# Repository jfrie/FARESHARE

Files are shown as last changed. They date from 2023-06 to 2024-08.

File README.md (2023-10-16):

# FARESHARE
Fluid tracking in socially housed rats



## Contents of Repository
- Build instructions
- 3D print files
- Arduino code
- PCB GERBER file

## Description
Social factors have been shown to play a significant role in alcohol consumption. Studying the role of social context on alcohol drinking is important to understand the factors that contribute to initiation or maintenance of casual and problematic alcohol use. A large body of preclinical research has shown that social environment plays an important role in alcohol consumption and preference, though the extent of these effects have been obfuscated by methodological differences and technical challenges. Robust individual differences in alcohol intake in socially housed animals are difficult to track when animals share a common fluid source. Commercial solutions are prohibitively expensive and are limited by proprietary software and hardware. Here we describe an affordable, open-source solution for tracking fluid consumption in socially housed rats. The device uses RFID to identify rats, a lickometer to activate fluid delivery, a custom low-profile PCB that sits on top of an Arduino-based microcontroller, fluid delivery via custom peristaltic pump for accurate measurement of consumption volume, OLED display, and continuous data logging to an SD card. Having a robust, affordable method for measuring drinking in socially housed animals will be of considerable use in preclinical addiction research and a step toward more translationally relevant animal models of fluid consumption. The added dimension of time allows for the analysis of circadian-linked consumption and the discrimination of continuous or binge-like drinking behaviours. Additionally, being open-source enables researchers to customize the device for more advanced applications such as sending signals to additional peripherals (e.g., optogenetic stimulation) or software on drinking initiation for time-locked or closed-loop interventions, manipulations, and measurements.

Citing FARESHARE: A preprint introducing the software is available on bioXriv, which should be cited accordingly. https://www.biorxiv.org/content/10.1101/2023.10.06.561248v1.full

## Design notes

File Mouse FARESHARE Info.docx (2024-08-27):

Mouse FARESHARE

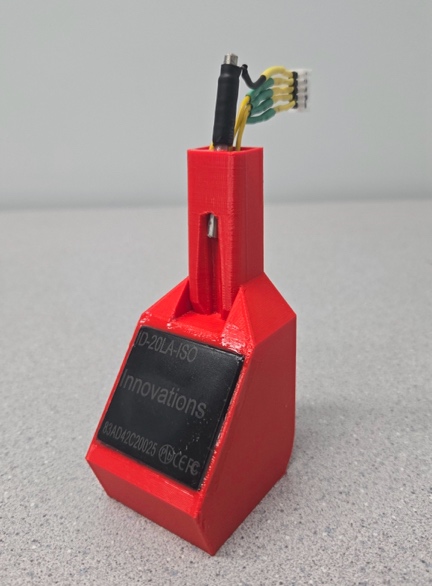
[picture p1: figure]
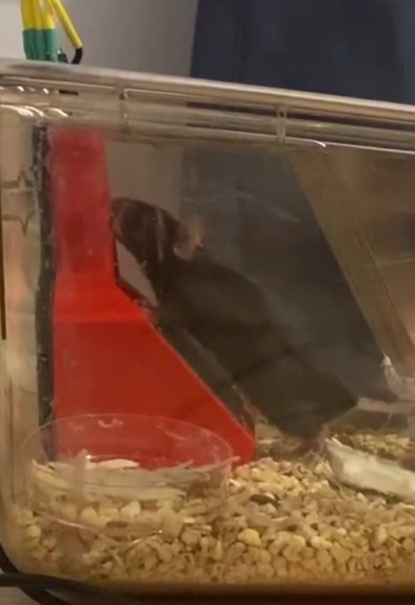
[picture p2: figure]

The mouse version of FARESHARE includes two notable design changes:

1) The scanner is now located below the subject such that the RFID tag can be placed on the chest. This frees the head for in vivo neural manipulation and recording.
2) Each lick now activates the motor such that increasing lick frequency increases fluid delivery. This means the licking microstructure is more meaningful, as the licking is driving fluid delivery, rather than just subject presence (with constant flow) as was the case previously.

The only major changes in instrumentation are the RFID housing print file, the scanner, and the straw.

The housing is now a single print. If printed upright (i.e. the direction it will be when used), it does not require any supports. We tried other designs, but mice would either find ways to cover the scanner, not align the tag properly, or just not use it.

The scanner used is now the larger ID20LA:

https://www.sparkfun.com/products/11828

Alternatively, ID20LA-ISO can be ordered directly from ID Innovations:

https://www.id-innovations.com/Modules(non%20write).htm

This is the same scanner but is compatible with the more standard ISO RFID tags that are commonly used in pets.

The straw is much smaller than the one used previously in rat version. We used these: https://www.amazon.ca/Unifizz-Stainless-Capillary-Seamless-Decoration/dp/B09PCY1L8N/ref=sr_1_13?keywords=stainless%2Bsteel%2Btube%2B3.2mm%2Bid&sr=8-13&th=1)

However, any 3.2mm ID, 4mm OD straw that is conductive will work. We cut them down to 5cm long with a Dremel. This size has the advantage of making a good seal with the tubing such that fluid does not drip through the straw, and rather is released in a more controlled droplet at the tip of the straw.

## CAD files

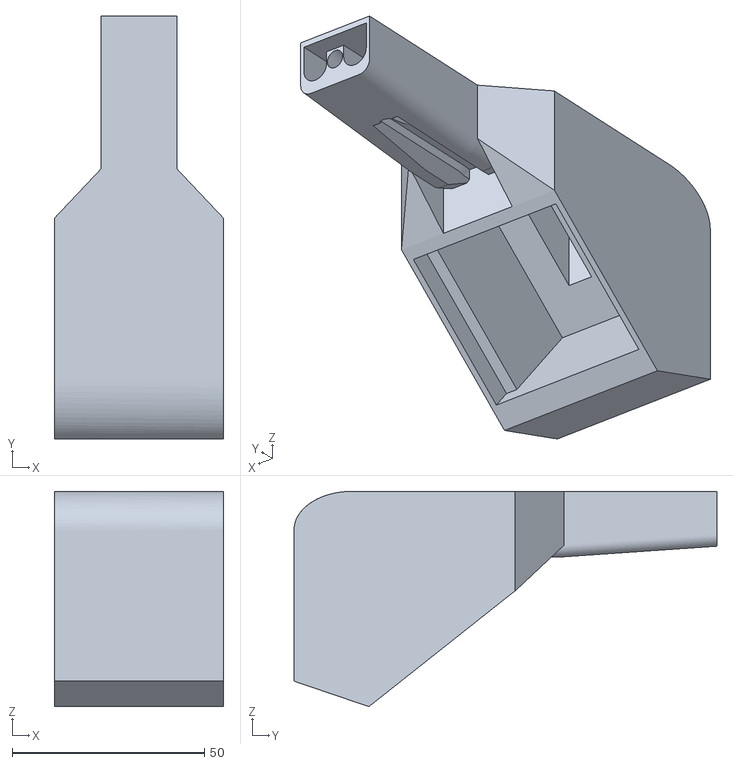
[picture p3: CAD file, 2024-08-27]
3D print files/Mouse RFID Housing.STL
44.0 x 110.0 x 56.0

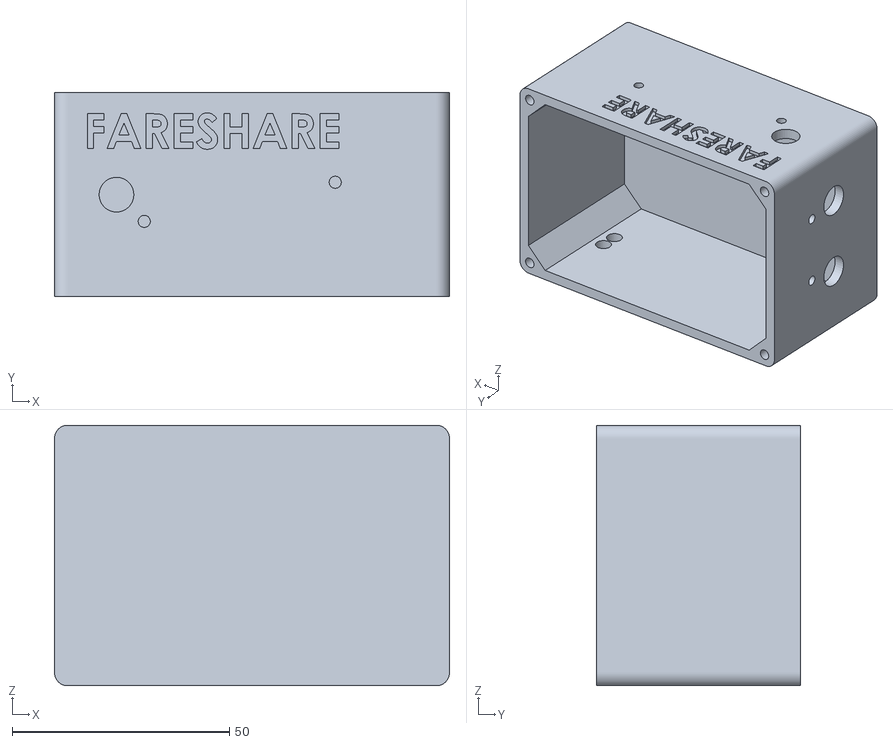
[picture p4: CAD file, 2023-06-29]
3D print files/Box.STL
91.0 x 47.0 x 60.0

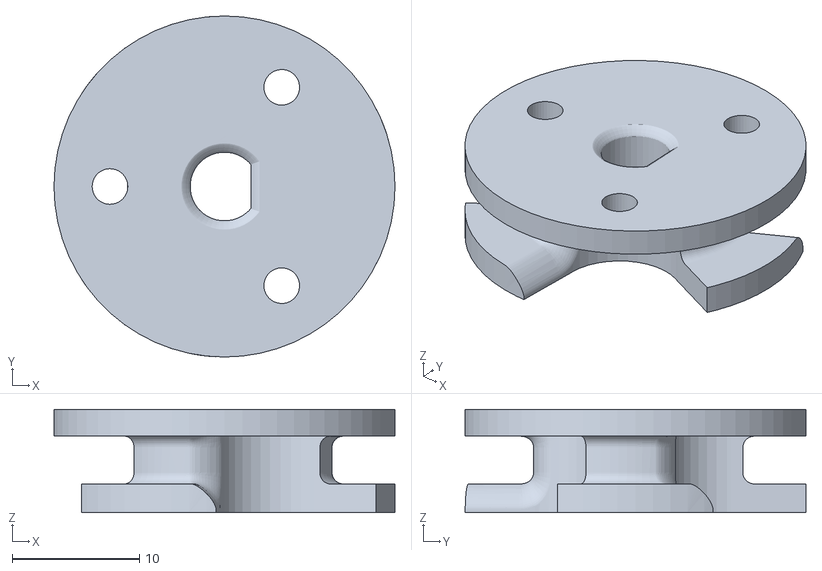
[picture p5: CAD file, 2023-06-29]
3D print files/Rotor.STL
26.8 x 26.8 x 8.10

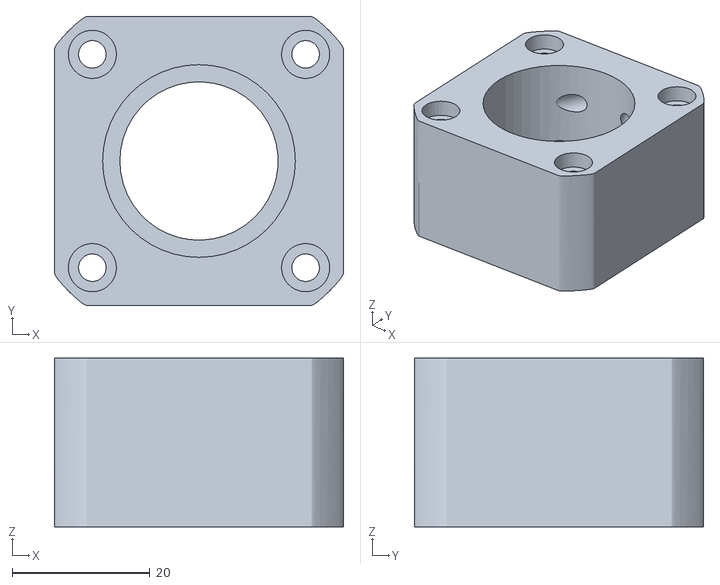
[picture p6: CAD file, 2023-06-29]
3D print files/Pump Case.STL
42.0 x 42.0 x 24.5

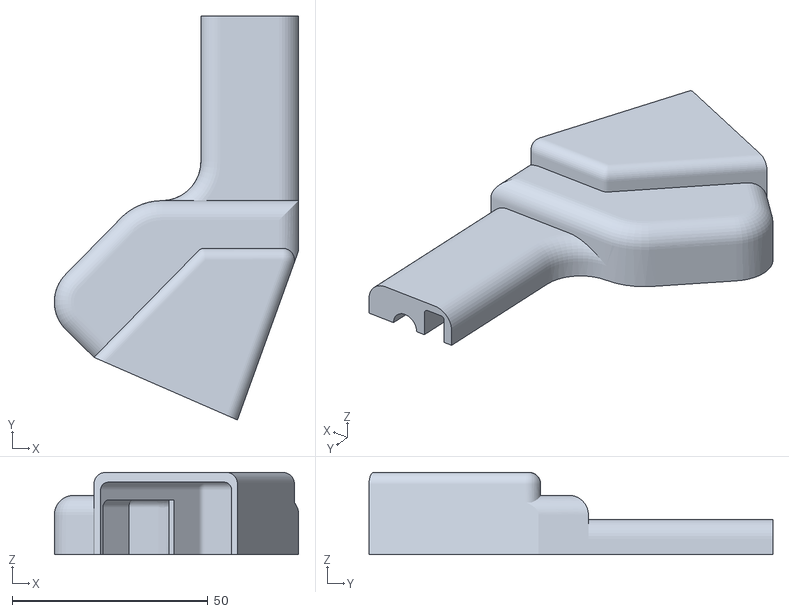
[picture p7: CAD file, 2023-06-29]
3D print files/RFID Housing Right.STL
62.4 x 103.2 x 21.0

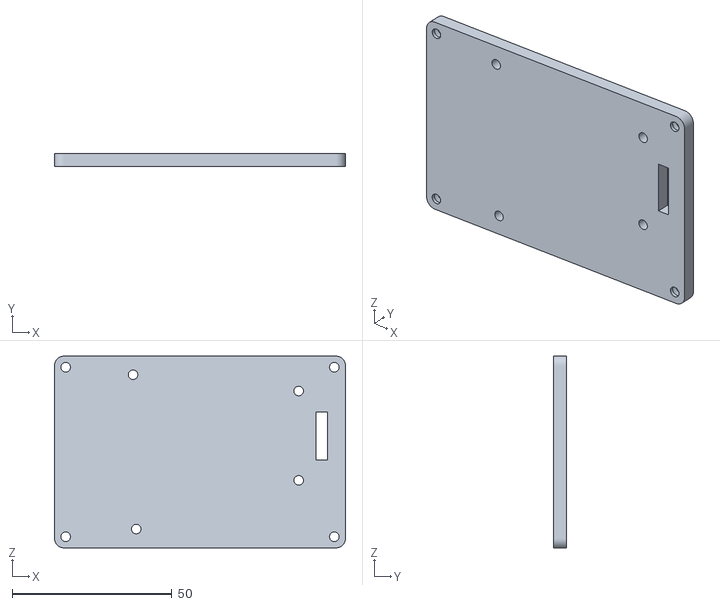
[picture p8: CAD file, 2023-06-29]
3D print files/Box_lid.STL
91.0 x 4.00 x 60.0

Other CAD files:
3D print files/RFID Housing Left.STL

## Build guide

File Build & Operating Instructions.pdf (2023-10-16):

Build Instructions

Table 1: Bill of Materials

Part Name | Distributer | Alternate | Cost ($US)
1000uF Capacitor (through hole) | Mouser | Digikey | 1.63
16G Needles (x2) | Fisher Scientific | Surgo | 0.85
1M Ohm Resistor (through hole) | Mouser | Digikey | 0.42
5-pin 2.54mm JST Female to Female
Cable | Walmart | Amazon | 1.30
5-pin 2.54mm JST Male header (x2) | Walmart | Amazon | 0.14
3D printer filament | Amazon | Hatchbox | 2.50
A4988 Stepper Motor Driver | Amazon | Digikey | 1.20
Ball bearings (3mm x 8mm x 4mm) (x4) | Amazon | NewEgg | 2.00
Barrel Jack PCB mount (3 pin) | Mouser | Digikey | 1.25
Break Away Headers (2.54mm straight)
(41 pins) | Sparkfun | Mouser | 3.50
Custom PCB | JLCPCB | OSHpark | 2.00
Dual lock (10cm) | Amazon | Mouser | 1.50
Epoxy | Walmart | Amazon | 6.12
Hook-up Wire (22 AWG) | Sparkfun | Amazon | 2.95
M3 Screw (Hex Socket, 25mm) (x4) | Home Hardware Amazon | 2.75
M3 Screw (Hex Socket, 10mm) (x7) | Home Hardware Amazon | 3.25
M3 Screw (Hex Socket, 5mm) (x8) | Home Hardware Amazon | 3.50
M3 Nut (x3) | Home Hardware Amazon | 2.00
Masterflex® Microbore Pump Tubing, Platinum-Cured Silicone, 1.42mm ID, 3.12mm OD (16cm long) | Avantor | Fisher
| | Scientific | 2.30
Mini 4-pin Push Button | Mouser | Amazon | 1.00
Micro SD Card (FAT16 or 32, 64MB to
32GB) | Amazon | Walmart | 5.99
Nema 17 Stepper Motor (4 lead, 2A) (17HS19-2004S1) | Amazon | AliExpress | 13.99
Power Supply (12V, 3A) | Amazon | Walmart | 8.99
Qwiic Cable Kit | Sparkfun | Mouser | 8.95
Qwiic OLED Display (0.91 in, 128x32) | Sparkfun | Mouser | 10.95
Qwiic OpenLog | Sparkfun | Mouser | 18.50
RedBoard Qwiic | Sparkfun | Mouser | 21.50
RFID Chip Injector (2.12x12mm) | Amazon | AliExpress | 6.99
RFID Glass Capsule (125kHz) | Sparkfun | Mouser | 5.50
RFID Reader Breakout | Sparkfun | Mouser | 2.10
RFID Reader ID-12LA (125 kHz) | Sparkfun | Mouser | 32.50
Silicone Tubing 1.5mm ID x 3mm (140
cm) | Amazon | NewEgg | 6.99
Stainless Steel Straw (straight 5mm OD) | Amazon | Whisk | 0.60
Total | | | $185.71

PCB Ordering: Upload GERBER file to https://jlcpcb.com and order with default settings.

PCB Soldering: The figure below shows the PCB before (left) and after (right) soldering. The

PCB is silk screened and labeled such that soldering orientation and positioning is clear.

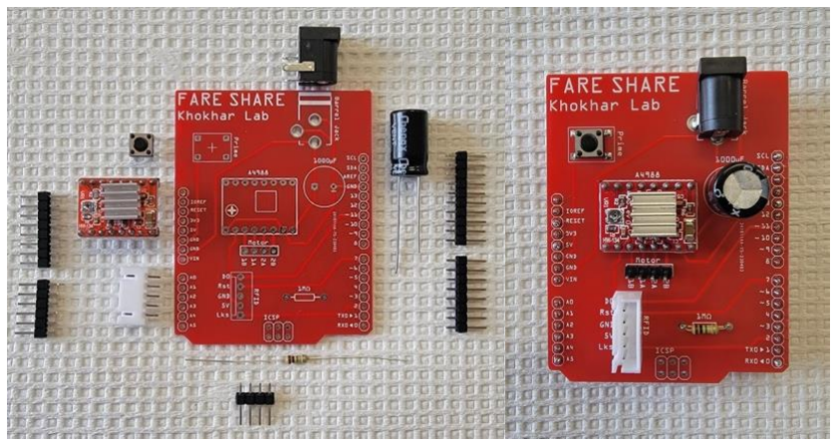
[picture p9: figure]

3D Printing: Print in the orientations shown below. The pump rotor and RFID housing should

be printed with supports. All other components can be printed without supports. Print with

standard PLA filament.

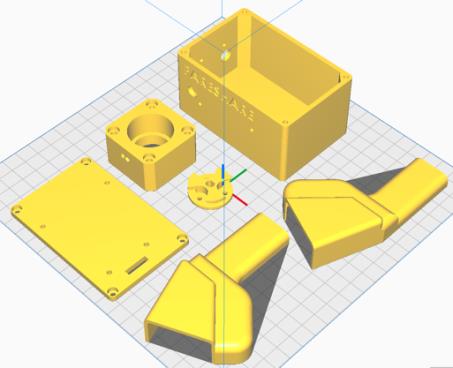
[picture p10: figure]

Pump Assembly:

1. Cut two 1cm pieces of needle by slowly rotating and cutting evenly so as not to

crimp.

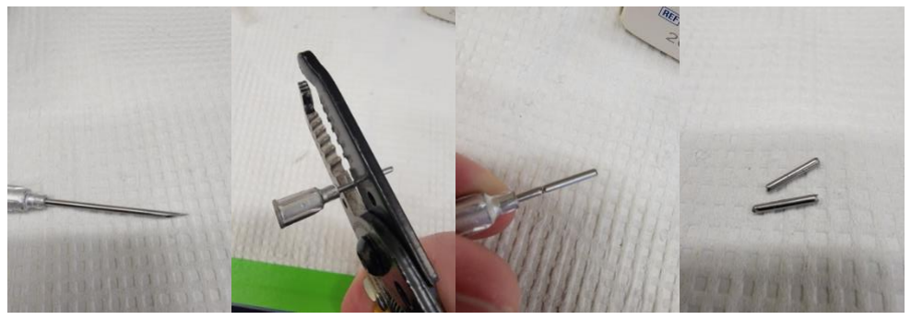
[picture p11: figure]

2. Screw M3X10 screws through the holes of the rotor

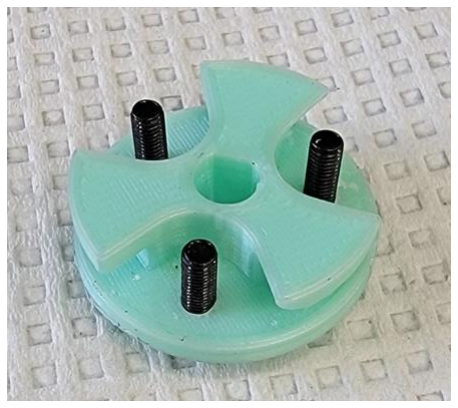
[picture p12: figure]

3. Place bearings on screws and secure with M3 nuts. Ensure the nuts are not too tight so

as to allow the bearings to turn without any friction.

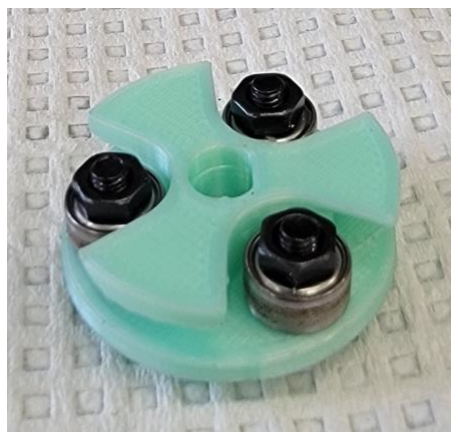
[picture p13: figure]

4. Thread 15cm segment of Masterflex tubing through pump case.

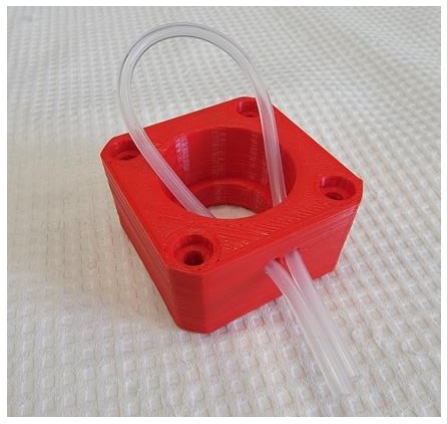
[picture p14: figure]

5. Wrap the tubing around the rotor and push the rotor into the pump housing while

keeping tension on the tubing. Once inside the housing, manually rotate the rotor a bit

and pull on each side of the tubing until the rotor is straight and the tubing wraps

around each bearing.

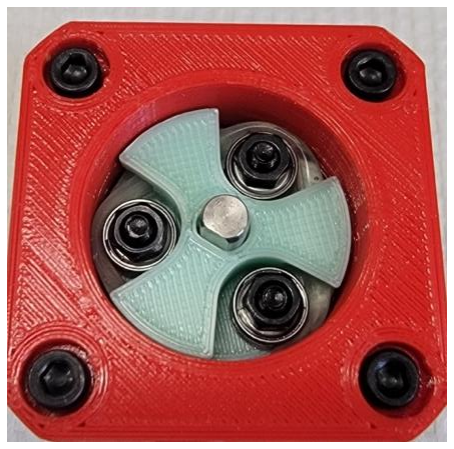
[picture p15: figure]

6. Thread another bearing onto the left (with tubing facing you) exiting tube.

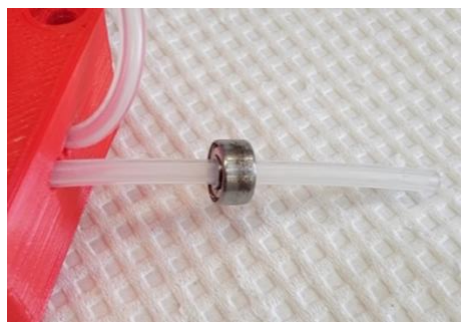
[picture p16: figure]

7. Bring bearing up to pump housing and epoxy or super glue to both tubing and

housing. This will keep the tubing from being pulled through the rotor or shifting.

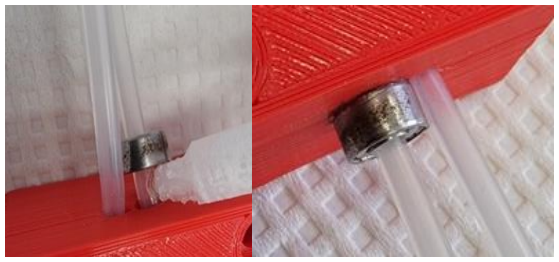
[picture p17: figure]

8. Insert needle segments halfway into tubing ends.

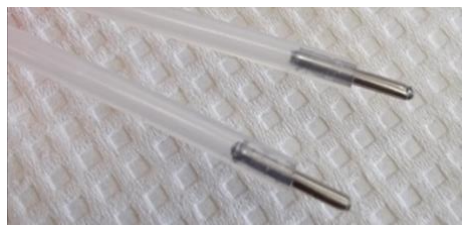
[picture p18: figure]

9. Place super glue where needle exits tubing and insert needle ends into two 70 cm

segments of silicon tubing (cheaper tubing), gluing tubes together.

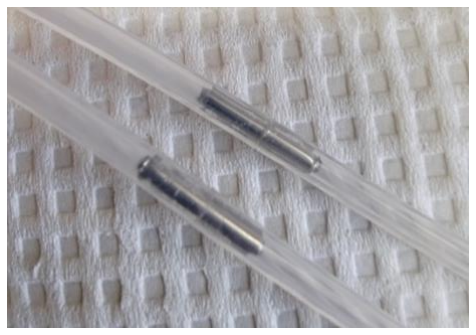
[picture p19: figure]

10. Place pump assembly onto motor with tubing facing the same direction as motor

wires and, using M3x25mm screws, fix in place.

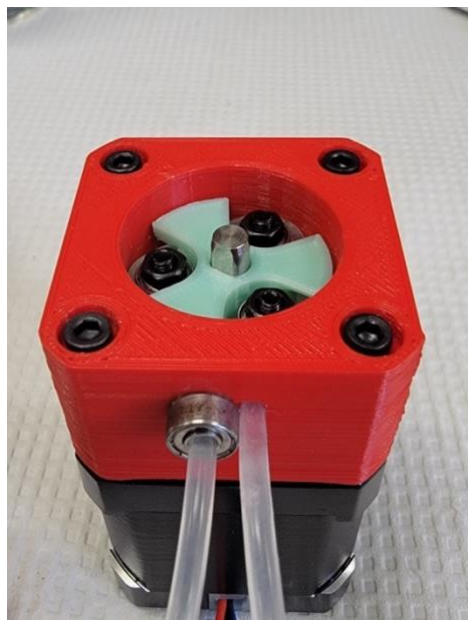
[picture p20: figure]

11. Place assembly into box, feeding tubing through input and output holes, and wrapping

most of the motor wiring together, placing it in the space between the motor and the

wall of the box. Spray the bearings and inner tubing generously with an all-purpose

lubricant.

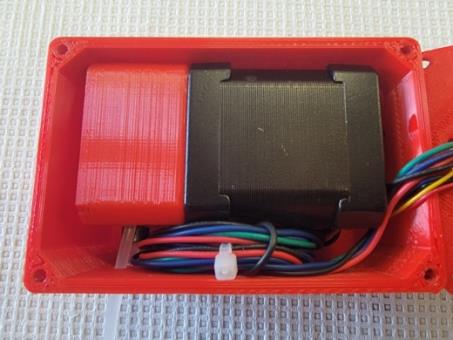
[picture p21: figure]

12. Attach OLED display to side of box with M3x4mm screws and thread 10cm Qwiic

cable from the left port on the OLED into box.

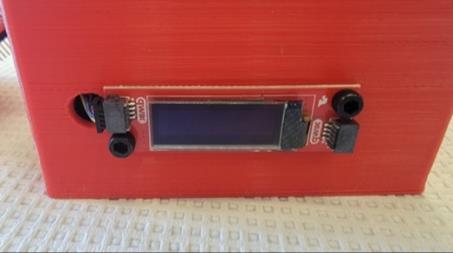
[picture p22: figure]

13. Attach data logger to the side of the box with M3x4mm screws and connect Qwiic

cable from OLED into right port of data logger. Connect left port to 5cm Qwiic cable.

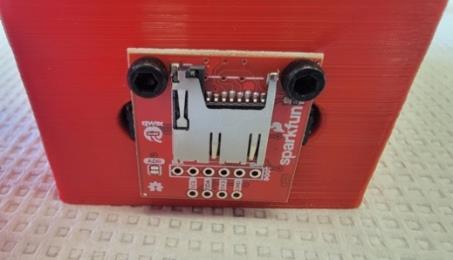
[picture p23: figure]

14. Attach RedBoard to box lid with M3x4mm screws. Feed motor wiring and Qwiic

cable from data logger through square channel in lid. Connect Qwiic cable to

RedBoard. Connect lid to box with M3x10mm screws.

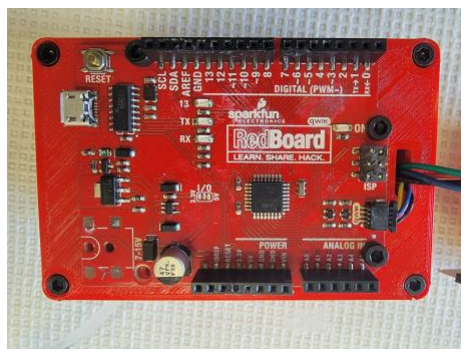
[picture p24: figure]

15. Plug PCB into RedBoard and connect motor wires to PCB motor pins with the black

wire closest to the resistor.

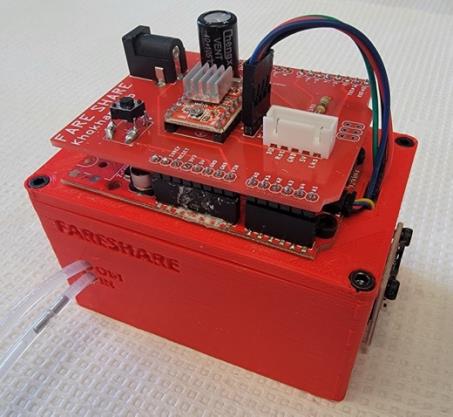
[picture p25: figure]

RFID Housing Assembly:

1. Solder RFID Breakout Board to RFID Reader.

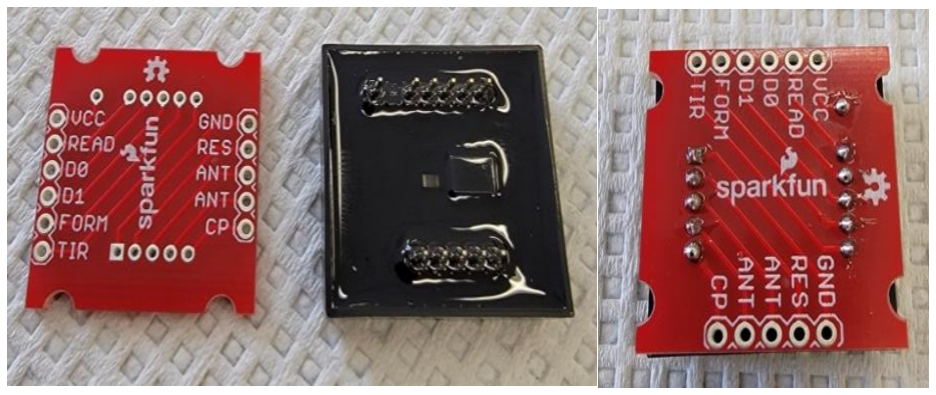
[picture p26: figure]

2. Solder a wire between the FORM and GND pins.

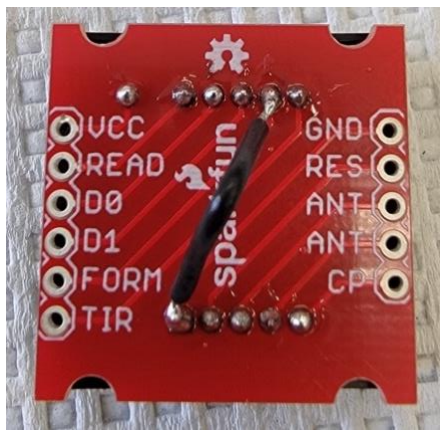
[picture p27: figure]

3. Solder 30cm segments of wire to Vcc, D0, GND, and RST through hole pins. Label

these wires at the unattached ends so you can identify them later on once they are

encased.

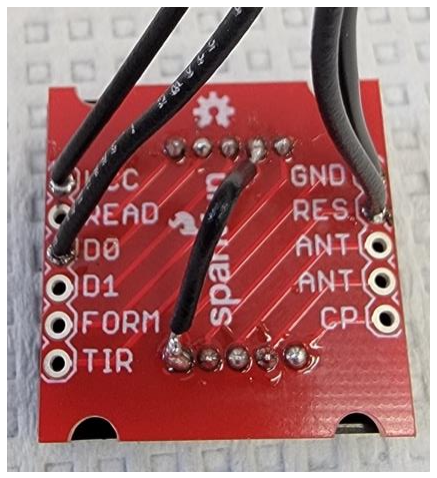
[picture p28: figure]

4. Epoxy the metal straw into one half of the RFID housing with 0.5cm of straw

projecting past the straw channel. Using glue or command strips, secure RFID sensor inside housing and thread wires through wire channel. Epoxy the other half of RFID

housing together.

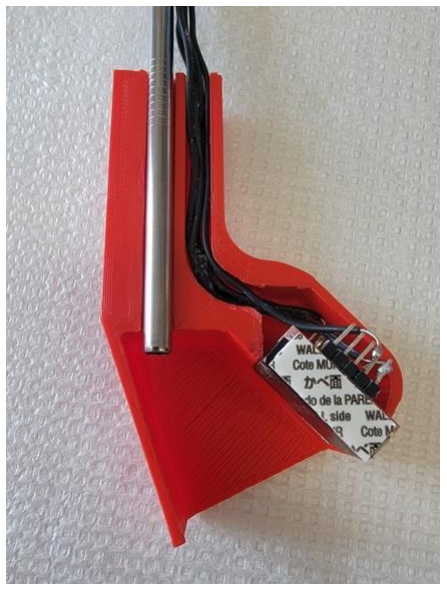
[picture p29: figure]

5. Cut the wires such that they are 2cm longer than the straw and, with the same

orientation as the plugin on the PCB, solder each wire to a JST header.

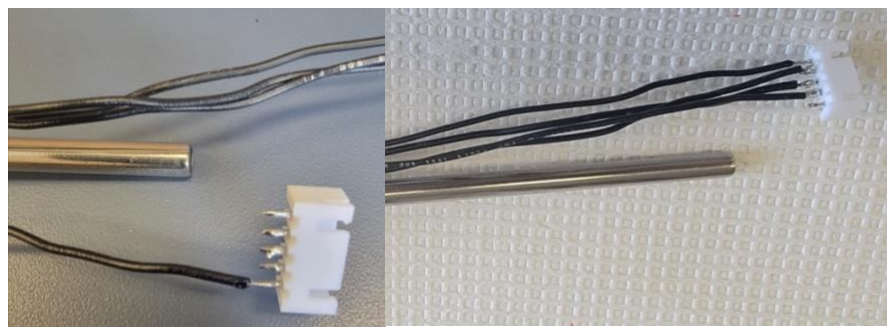
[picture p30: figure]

6. Strip 15cm off a 20cm wire. Wrap the stripped section around the tip of the straw and

secure with electrical tape. Cut the wire to line up with the remaining pin on the JST

header and solder.

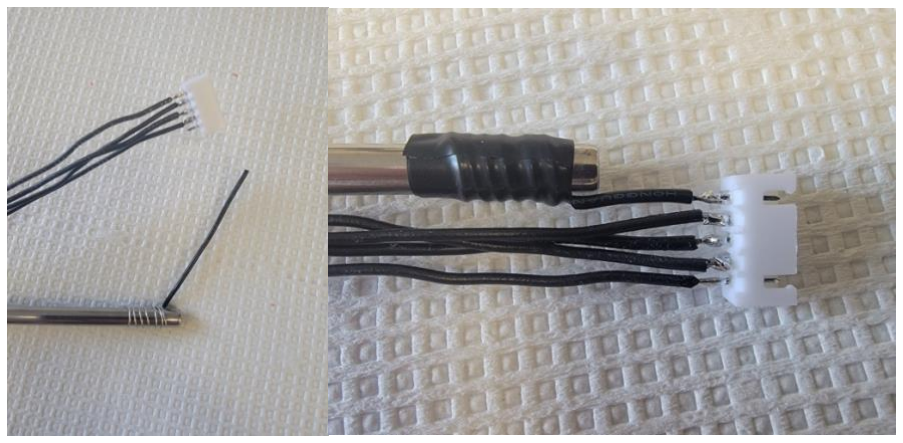
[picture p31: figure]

7. Use electrical tape to secure all wire to the straw.

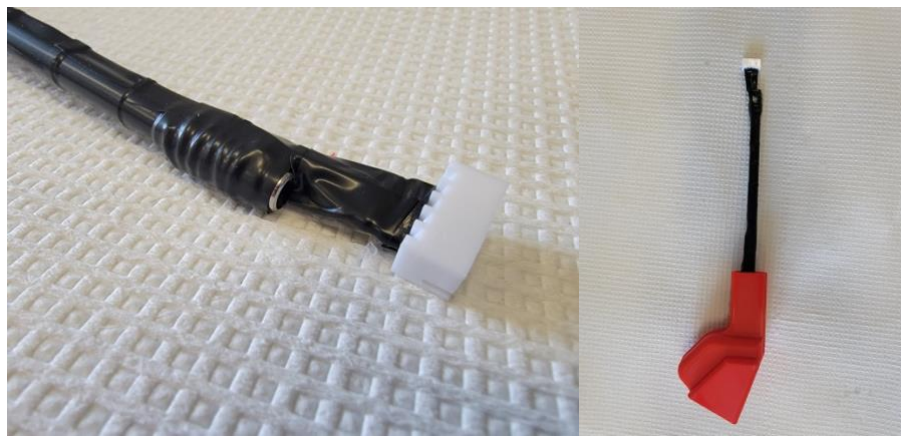
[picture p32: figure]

Load libraries: In the Arduino IDE select Tools>Manage Libraries. In the library manager,

download Adafruit GFX Library, Adafruit SSD1306, SparkFun Qwiic OpenLog, and

CapacitiveSensor.

Addition of RFID Tags to Code: Upload FARESHARE.ino to RedBoard Qwiic. Open serial

monitor and place new RFID tag under RFID sensor. The serial monitor will display the new

tag ID. Copy this ID and use it to replace the ID on line 38 of the code. Do this for each tag in

the following lines for as many rats as are being tracked. Add one additional tag that will be

used for priming the pump tubing with fluid when starting an experiment. Note: FARESHARE

can track as many animals as needed; however, the OLED display only has room to show the

overall results of the first four rats.

Pump Calibration: Each assembled peristaltic pump will be slightly different due to small

inconsistencies in 3D printing and assembly. Therefore, to ensure each pump delivers an

accurate volume and at the same rate, the pumps must be calibrated by the following

instructions:

1. Place the input tube into a container of water and the output into a beaker that is at least

10mL.

2. Prime the line using the push button.
3. Place the beaker with the output tube onto an analytical scale.
4. Place an RFID tag by the RFID sensor and tap the straw with your finger to activate the

motor. Time how long it takes for FARESHARE to deliver 10g of water.

5. Plug this time in seconds into the following formula: Scalemotor =

420
time

and set the

motor_scale variable on line 83 to this new value and upload the new code. This will

ensure each device takes the same amount of time to dispense fluid (~7 minutes for

10mL).

6. Tare the scale and fill it to 10g again with the pump.
7. Plug the volume reading on the FARESHARE OLED display into the following

formula: Scaleflow =

10
volume

and set the flow_scale variable on line 81 to this new

value and upload the new code.

Operating instructions

1. Prior to starting experiments, remove any .csv or .txt files from the SD card. Insert the

SD card into the SD card slot on the Qwiic OpenLog. Note: The Qwiic OpenLog SD

card logger used in FARESHARE is compatible with 64MB to 32GB microSD cards

in either FAT16 or FAT32 formats.

2. Attach straw section of FARESHARE to inside of cage with type 400 dual lock, feeding

top of straw through the cage top.

3. Connect wires to PCB via 5-pin JST cable.
4. Place input tube into fluid reservoir and tape in place
5. Plug power supply into the wall and connect the barrel connector to the barrel jack on

the PCB. Note: Ensure SD card is in reader prior to plugging as files are created when

device powers up.

6. Press the reset button on the Arduino to begin the experiment. Note: make a note of the

time that the experiment is started as the timestamps for each drinking bout are

measured in milliseconds following this moment.

7. Place the priming tag onto the RFID sensor to operate the pump until fluid has fully

filled the line.

8. Place output tube ~6cm into straw and tape in place.
9. Allow rats to drink as long as desired.
10. When experiment is complete, unplug FARESHARE and remove SD card.

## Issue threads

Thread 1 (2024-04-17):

### ISSUE TITLE
share editable files for PCB?

### ISSUE THREAD

**Issue by amchagas** [jfrie/FARESHARE#1]
Hi!

thanks for putting up all the doc for this device, really cool and well outlined! 

we are looking into implementing the system for mice for one of the labs in Sussex, and we also thought about adding a load cell to the system so we can automatically weight the animals. for that it would be useful to have editable files for the PCB... is this something you could share? which softwrae did you use to create it? Thanks!

**Comment by jfrie** [comment]
Hey,

Great point! Definitely an oversight. I've now uploaded an .fzz file to the GitHub so it can be easily modified. I made it in Fritzing.

Cheers,
Jude


Jude Frie | PhD

The Khokhar Lab, Department of Biomedical Sciences

University of Guelph, Ontario, Canada

________________________________
From: Andre Maia Chagas ***@***.***>
Sent: Wednesday, April 17, 2024 9:31 AM
To: jfrie/FARESHARE ***@***.***>
Cc: Subscribed ***@***.***>
Subject: [jfrie/FARESHARE] share editable files for PCB? (Issue #1)


CAUTION: This email originated from outside of the University of Guelph. Do not click links or open attachments unless you recognize the sender and know the content is safe. If in doubt, forward suspicious emails to ***@***.***


Hi!

thanks for putting up all the doc for this device, really cool and well outlined!

we are looking into implementing the system for mice for one of the labs in Sussex, and we also thought about adding a load cell to the system so we can automatically weight the animals. for that it would be useful to have editable files for the PCB... is this something you could share? which softwrae did you use to create it? Thanks!

**Comment by amchagas** [comment]
thanks!

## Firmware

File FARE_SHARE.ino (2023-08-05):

#include <SoftwareSerial.h>
#include <SPI.h>
#include <Wire.h>
#include <Adafruit_GFX.h>
#include <Adafruit_SSD1306.h>
#include "SparkFun_Qwiic_OpenLog_Arduino_Library.h"
#include <CapacitiveSensor.h>

// define capacitive sensor pins
#define sensePin 2
#define sendPin 3

// Create capacitive sensor object
CapacitiveSensor cap_val = CapacitiveSensor(sendPin,sensePin); 

// A4988 control pins
#define dirPin 4  // Direction
#define stepPin 5 // Step

// LED display setup
#define SCREEN_WIDTH 128 // OLED display width, in pixels
#define SCREEN_HEIGHT 32 // OLED display height, in pixels
#define OLED_RESET -1 // Reset pin # (or -1 if sharing Arduino reset pin)
#define SCREEN_ADDRESS 0x3C ///< See datasheet for Address; 0x3D for 128x64, 0x3C for 128x32
Adafruit_SSD1306 display(SCREEN_WIDTH, SCREEN_HEIGHT, &Wire, OLED_RESET);

// set pin for reseting RFID
#define RFIDResetPin 7

// set pin for button press
#define buttonPin 8

// set pins for software serial
#define RX 11
#define TX 12

// set RFID tag length
#define tagLength 13

// create instance of logger
OpenLog logger;

// known RFID tags: replace, add, or remove tag IDs as required. 
// It is currently configured for 4 rats and a tag for priming the pump tubing.
//******************************************************************************************** try adding additional tags and see if effects volume
//char tag1[tagLength] = "000C9524F04D"; // rat 1 tag, comment when testing
char tag2[tagLength] = "000C9523A11B"; // rat 2 tag, comment when testing
char tag3[tagLength] = "000C952547FB"; // rat 3 tag
char tag4[tagLength] = "000C9523BF05"; // rat 4 tag

//char tag5[tagLength] = ""; // next rat tag 

char tag1[tagLength] = "000C9522D962"; // tag for testing, comment when not testing

char tagString[tagLength]; // new tag place holder

// Total drinking volumes for each rat. Add or remove for the # of rats being used.
float rat_1_total_volume = 0;
float rat_2_total_volume = 0;
float rat_3_total_volume = 0;
float rat_4_total_volume = 0;
// float rat_5_total_volume = 0;

// Total number of licks for each rat. Add or remove for the # of rats being used.
int rat_1_total_licks = 0;
int rat_2_total_licks = 0;
int rat_3_total_licks = 0;
int rat_4_total_licks = 0;
// int rat_5_total_licks = 0;

// Initializing variables to 0
int licks = 0;
long cap_value = 0;
float bout_volume = 0;
unsigned long bout_start = 0;
int tick = 0;
unsigned long start = 0;

// flow_scale and motor_scale may need to be adjusted for volume measurement and rate to be accurate
float flow_scale = 1;
float flow_rate = 0.00744 * flow_scale;
float motor_scale = 1;
int motor_speed = 16450 + (motor_scale * 850);

// Instantiate software serial
SoftwareSerial serial(RX,TX); 

void setup(){

  pinMode(buttonPin, INPUT_PULLUP); // set button pin as input with a pull up resistance
  
  //logger file setup
  Wire.begin();
  logger.begin();
  
  // setup file for rat 1
  logger.append("rat1_drinking_data.csv");
  logger.print("Start Time (ms)");
  logger.print(",");
  logger.print("End Time (ms)");
  logger.print(",");
  logger.print("Bout Volume (mL)");
  logger.print(",");
  logger.println("Bout Licks");
  logger.syncFile();

  // setup file for rat 2
  logger.append("rat2_drinking_data.csv");
  logger.print("Start Time (ms)");
  logger.print(",");
  logger.print("End Time (ms)");
  logger.print(",");
  logger.print("Bout Volume (mL)");
  logger.print(",");
  logger.println("Bout Licks");
  logger.syncFile();

  // setup file for rat 3
  logger.append("rat3_drinking_data.csv");
  logger.print("Start Time (ms)");
  logger.print(",");
  logger.print("End Time (ms)");
  logger.print(",");
  logger.print("Bout Volume (mL)");
  logger.print(",");
  logger.println("Bout Licks");
  logger.syncFile();

  // setup file for rat 4
  logger.append("rat4_drinking_data.csv");
  logger.print("Start Time (ms)");
  logger.print(",");
  logger.print("End Time (ms)");
  logger.print(",");
  logger.print("Bout Volume (mL)");
  logger.print(",");
  logger.println("Bout Licks");
  logger.syncFile();

  // Additional rats can be added here
  // logger.append("rat5_drinking_data.csv");
  // logger.print("Start Time (ms)");
  // logger.print(",");
  // logger.print("End Time (ms)");
  // logger.print(",");
  // logger.print("Bout Volume (mL)");
  // logger.print(",");
  // logger.println("Bout Licks");
  // logger.syncFile();
  
  // Setup motor control pins as Outputs
  pinMode(stepPin,OUTPUT); 
  pinMode(dirPin,OUTPUT);

  // set motor clockwise
  digitalWrite(dirPin,HIGH);
  
  // start serials
  serial.begin(9600);

  // LED display settings and initialization
  display.begin(SSD1306_SWITCHCAPVCC, SCREEN_ADDRESS);
  display.setTextSize(1);
  display.setTextColor(SSD1306_WHITE,SSD1306_BLACK);
  display.clearDisplay();
  updateDisplayRat1();
  updateDisplayRat2();
  updateDisplayRat3();
  updateDisplayRat4();
  display.display();

  // set reset pin high as default (keeps RFID on)
  pinMode(RFIDResetPin, OUTPUT);
  digitalWrite(RFIDResetPin, HIGH);
}

void loop(){
  
  // if priming button is pushed, activate motor 20 times
  byte buttonState = digitalRead(buttonPin);
  if (buttonState == LOW){
    for (int i=0; i<20; i++) {
    activate_motor();
    }
  }
  
  // Auto updates the display every 150 loops. Important for returning to normal function after reading an unknown tag. 
  tick++;
  if (tick % 150 == 0){
    display.clearDisplay();
    updateDisplayRat1();
    updateDisplayRat2();
    updateDisplayRat3();
    updateDisplayRat4();
    tick = 0;
  }

  readTag(); // read tag
  checkTag(tagString); // check if match
  clearTag(tagString); // clear tag
  resetReader(); // reset the RFID reader
}

//Check tag against known tags
void checkTag(char tag[]){

  // When no tag is present, bout is over. Reinitialize licks and bout volume to 0.
  if (strlen(tag) == 0) {
    bout_volume = 0;
    licks = 0;
    delay(200);
    return;
  }

  // rat 1
  //********************************************************
  if (compareTag(tag, tag1)) { // if senses tag 1
    
    // timer for last tag read
    start = millis();
   
    // record bout start time
    bout_start = millis();

    while ((compareTag(tag, tag1)) || (((millis()-start) < 800))){ // While the tag present is being sensed or less than 800ms has passed since tag present 
      
      // reset timer if tag is sensed
      if (compareTag(tag, tag1)){
        start = millis();
      }
     
      // prepare RFID for next read
      clearTag(tagString);
      resetReader();
      
      // count licks
      cap_value = cap_val.capacitiveSensor(50);
      if (cap_value>100){
       licks++;
       rat_1_total_licks++;
      }

      // bout begins on first lick
      if (licks>0){ 

        // turn motor
        activate_motor();
      
        // calculate bout volume
        bout_volume = bout_volume + flow_rate; 
      
        // calculate total volume
        rat_1_total_volume = rat_1_total_volume + flow_rate;

        // update display
        updateDisplayRat1();
        delay(200);
      }
      // read tag again
      readTag();

    }

    // log bout data
    if (licks>0){
      logger.append("rat1_drinking_data.csv");
      logger.print(bout_start);
      logger.print(",");
      logger.print(millis());
      logger.print(",");
      logger.print(bout_volume,4);
      logger.print(",");
      logger.println(licks);
      logger.syncFile();
    }

  //********************************************************

  // rat 2
  //********************************************************
  } else if (compareTag(tag, tag2)) {
    start = millis();
    bout_start = millis();
    while ((compareTag(tag, tag2)) || (((millis()-start) < 800))){
      if (compareTag(tag, tag2)){
        start = millis();
      }
      clearTag(tagString);
      resetReader();
      cap_value = cap_val.capacitiveSensor(50);
      if (cap_value>100){
       licks++;
       rat_2_total_licks++;
      }
      if (licks>0){
        activate_motor();
        bout_volume = bout_volume + flow_rate;
        rat_2_total_volume = rat_2_total_volume + flow_rate;
        updateDisplayRat2();
        delay(200);
      }
      readTag();
    }
    if (licks>0){
      logger.append("rat2_drinking_data.csv");
      logger.print(bout_start);
      logger.print(",");
      logger.print(millis());
      logger.print(",");
      logger.print(bout_volume,4);
      logger.print(",");
      logger.println(licks);
      logger.syncFile();
    }
  //********************************************************

  // rat 3
  //********************************************************
  } else if (compareTag(tag, tag3)) { 
    start = millis();
    bout_start = millis();
    while ((compareTag(tag, tag3)) || (((millis()-start) < 800))){
      if (compareTag(tag, tag3)){
        start = millis();
      }
      clearTag(tagString);
      resetReader();
      cap_value = cap_val.capacitiveSensor(50);
      if (cap_value>100){
       licks++;
       rat_3_total_licks++;
      }
      if (licks>0){
        activate_motor();
        bout_volume = bout_volume + flow_rate;
        rat_3_total_volume = rat_3_total_volume + flow_rate;
        updateDisplayRat3();
        delay(200);
      }
      readTag();
    }
    if (licks>0){
      logger.append("rat3_drinking_data.csv");
      logger.print(bout_start);
      logger.print(",");
      logger.print(millis());
      logger.print(",");
      logger.print(bout_volume,4);
      logger.print(",");
      logger.println(licks);
      logger.syncFile();
    }
  //********************************************************

  // rat 4
  //********************************************************
  } else if (compareTag(tag, tag4)) {
    start = millis();
    bout_start = millis();
    while ((compareTag(tag, tag4)) || (((millis()-start) < 800))){
      if (compareTag(tag, tag4)){
        start = millis();
      }
      clearTag(tagString);
      resetReader();
      cap_value = cap_val.capacitiveSensor(50);
      if (cap_value>100){
       licks++;
       rat_4_total_licks++;
      }
      if (licks>0){
        activate_motor();
        bout_volume = bout_volume + flow_rate;
        rat_4_total_volume = rat_4_total_volume + flow_rate;
        updateDisplayRat4();
        delay(200);
      }
      readTag();
    }
    if (licks>0){
      logger.append("rat4_drinking_data.csv");
      logger.print(bout_start);
      logger.print(",");
      logger.print(millis());
      logger.print(",");
      logger.print(bout_volume,4);
      logger.print(",");
      logger.println(licks);
      logger.syncFile();
    }
  //********************************************************

  // Additional rat
  //********************************************************
  // } else if (compareTag(tag, tag5)) {
  //   start = millis();
  //   bout_start = millis();
  //   while ((compareTag(tag, tag5)) || (((millis()-start) < 800))){
  //     if (compareTag(tag, tag5)){
  //       start = millis();
  //     }
  //     clearTag(tagString);
  //     resetReader();
  //     cap_value = cap_val.capacitiveSensor(50);
  //     if (cap_value>100){
  //      licks++;
  //      rat_5_total_licks++;
  //     }
  //     if (licks>0){
  //      activate_motor();
  //      bout_volume = bout_volume + flow_rate;
  //      rat_5_total_volume = rat_5_total_volume + flow_rate;
  //      updateDisplayRat5();
  //      delay(200);
  //     }
  //     readTag();
  //   }
  //  if (licks>0){
  //    logger.append("rat5_drinking_data.csv");
  //    logger.print(bout_start);
  //    logger.print(",");
  //    logger.print(millis());
  //    logger.print(",");
  //    logger.print(bout_volume,4);
  //    logger.print(",");
  //    logger.println(licks);
  //    logger.syncFile();
  //  }
  //********************************************************
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

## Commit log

2023-06-29 Upload Arduino Code
2023-06-29 Upload 3D print files
    [Box.STL, Box_lid.STL, Pump Case.STL, RFID Housing Left.STL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]
2023-08-05 Updated Arduino Code
2024-04-17 Add Fritzing file
    [FARESHARE PCB.fzz]
2024-07-18 Updated PCB
    Now runs RFID scanner on 3.3V instead of 5V. Increases range and reliability.
    [FARESHARE PCB 2.1.fzz]
2024-07-18 Alternate code to drive motor on each lick
    Instead of providing continuous delivery of fluid when a drinking event is initiated, this code releases a small amount of fluid on each successive lick. This is more similar to the way a traditional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
